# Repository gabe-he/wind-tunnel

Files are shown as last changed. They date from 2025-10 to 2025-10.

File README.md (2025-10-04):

# Wind Tunnel Project

A wind tunnel is a device that produces a controlled stream of air to study how objects interact with airflow, for exploring the principles of aerodynamics.

This project aims to build an accessible, modular educational wind tunnel that can be easily transported and assembled, allowing demonstrations in classrooms, community centers, and public events. By bringing this interactive learning tool to underserved and low-income students, the project seeks to spark curiosity, deepen understanding of science, and inspire the next generation of innovators.

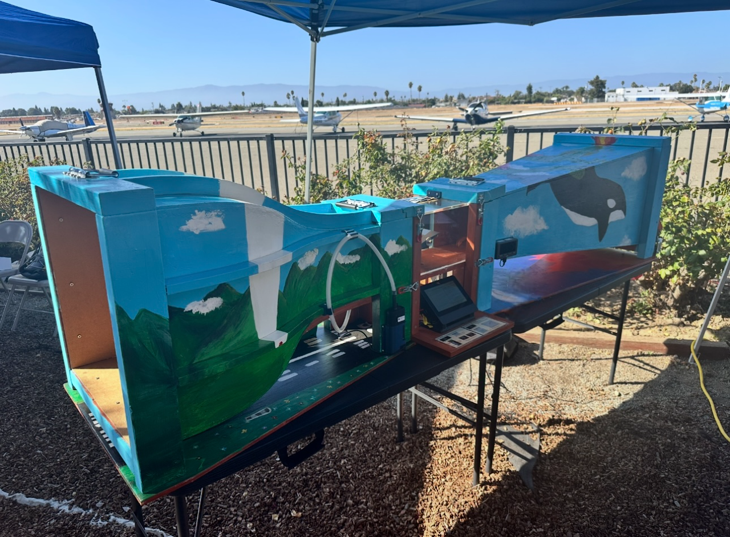
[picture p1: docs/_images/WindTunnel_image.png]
wind tunnel


This repository provides **all resources** related to the wind tunnel project — from planning and design to implementation and analysis. It is intended as a **comprehensive educational package** for anyone interested in building and studying a small-scale aerodynamic experiment. By sharing our design, data, and methods openly, I hope to make hands-on science learning more engaging and approachable for students, educators, and enthusiasts alike.

## Features

* Modular design, can be disassembled for easy transportation
* Adjustable wing angle
* Adjustable airflow speed
* Lift/Drag measurement to measure the lift/drag
* Smoke generator for clear visualization of streamlines
* Demonstrates fundamentals of aerodynamic lift and drag
  * Role of angle of attack in lift generation
  * How flow separation causes stall
  * Visual comparison of laminar vs turbulent flow

## Repository Structure

* [Hardware/](Hardware/) : Hardware design files
* [Software/](Software/) : Software
* [docs/](docs/) : Documentation

### Getting Start

You can start from [docs/](docs/)

### Contributing

Contributions are welcome!

If you have any questions, suggestions, or issues, please don’t hesitate to open an issue.

## Acknowledgements

This project was created by Gabrielle He as the Scout Eagle Project.

⭐️If you like this project, don't forget to give it a ⭐️!

Special thanks to:

* Ms. Catherine Liu @ [cpmentorship](https://www.cpmentorship.org/) – for representing an organization dedicated to mentoring youth and serving the community.
* Mr. Edwin El-Kareh – for his generous assistance and continuous support during the design and build process.
* Mr. Dean McCully @ [EAA62](https://www.eaa62.org/index.php?url=/contact.php) – Young Eagles Coordinator, for helping connect the project to meaningful community service opportunities.
* Mr. David Overhauser – for his expert guidance and instruction throughout the project.
* Mr. Biao – for his hands-on help in constructing the wind tunnel.
* [Troop 688](https://sites.google.com/view/troop688/) – for all the support that made this project possible.

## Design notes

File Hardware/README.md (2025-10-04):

# Hardware

This directory contains the hardware design files for the Wind Tunnel project.

* [windtunnel.FCStd](windtunnel.FCStd) : 3D CAD model of the wind tunnel, created using FreeCAD 1.0.1.
* [BOM.ods](BOM.ods) : Bill of Materials (BOM) of all parts needed to build the wind tunnel. Google sheets exported ods format.
* [BOM_images/](BOM_images/) : Images of parts in the BOM to help identify the parts.
* [Electrical/](Electrical/) : Schematic diagram of the test platform electrical circuit, and some sample images of the circuit.
* [3D_Print/](3D_Print/) : CAD and STL files for 3D printing the custom parts of the wind tunnel.
* [Datasheets/](Datasheets/) : Datasheets of some components used in the wind tunnel.
* [Contraction_Curve_Drawings.pdf](Contraction_Curve_Drawings-desmos.com.pdf) : The Contraction Curve Drawings.

## Build Instructions

User should first read the [Project Plan](../docs/Project_Plan.md) for the detailed design ideas.

Then user can refer to the 3D CAD model file [windtunnel.FCStd](windtunnel.FCStd) to build the wind tunnel hardware. The dimensions in the CAD model are accurate.

If need to know detailed information of each part, check the [BOM](BOM.ods). The part name in the BOM matches the part name in the CAD model.

## Sample Images

overall image of the wind tunnel:

wind tunnel

Sample image for the test platform:

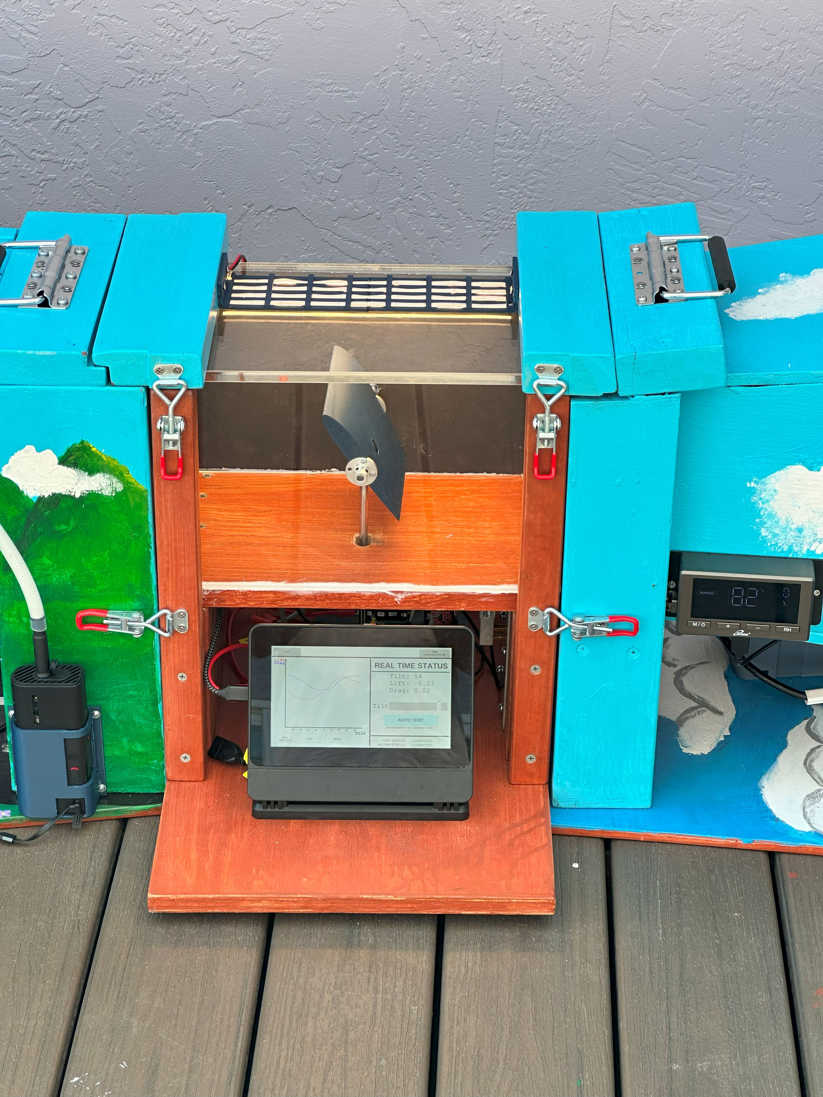
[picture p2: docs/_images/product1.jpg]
test platform


Sample image for the back side of test platform:

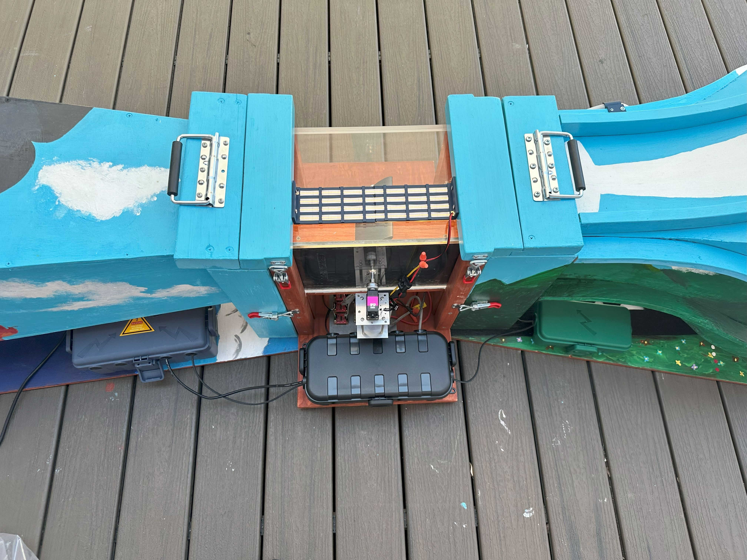
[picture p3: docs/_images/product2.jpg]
test platform back


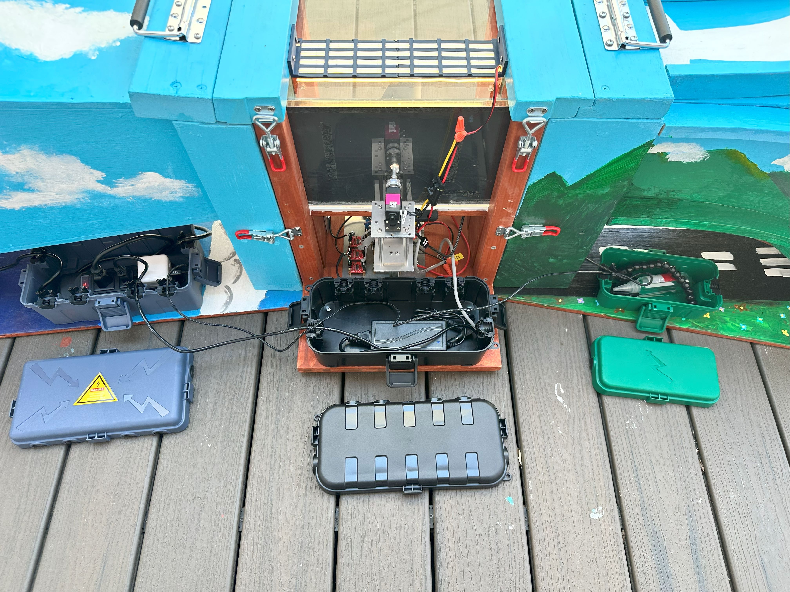
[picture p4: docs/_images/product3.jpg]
test platform back1


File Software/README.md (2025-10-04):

# Software

This is the Software portion of the Wind Tunnel project.

* [RaspberryPi/](RaspberryPi/): The main controller, a Raspberry Pi 4 with touchscreen display.
* [Pico/](Pico/): The microcontroller, a Raspberry Pi Pico, connect to three load cells and output force measurement results to Raspberry Pi 4.

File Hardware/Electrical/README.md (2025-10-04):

# Electrical

This directory contains the Electrical Circuit design files for the Wind Tunnel project.

* [Schematic.pdf](Schematic.pdf): the schematic diagram of the test platform's electrical circuit.
* [Schematic.svg](Schematic.svg): SVG version of same schematic for easy viewing.

The circuit components are mounted on an aluminum plate, using M2/M3/M4 standoffs to separate the components from the surface.

The aluminum plate is then secured to the test platform baseboard using wood screws.

Below is the image of the build::

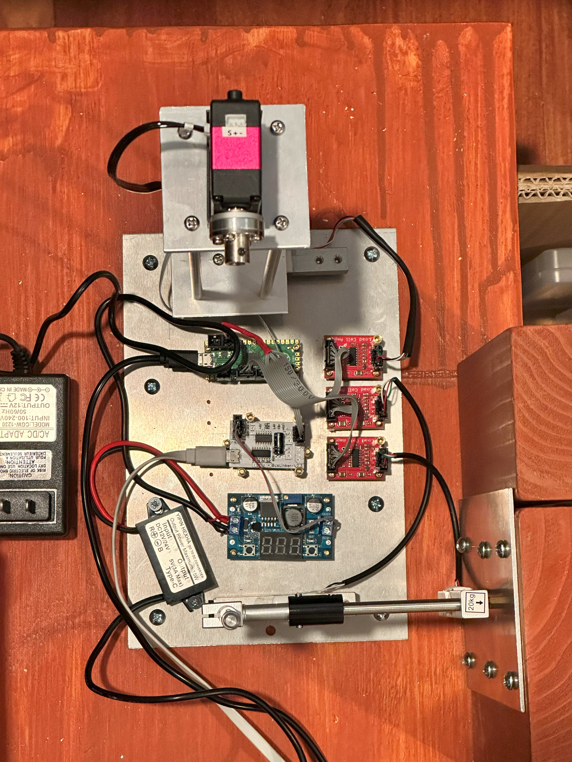
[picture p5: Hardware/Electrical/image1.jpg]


Below is the image before mounting to the baseboard:

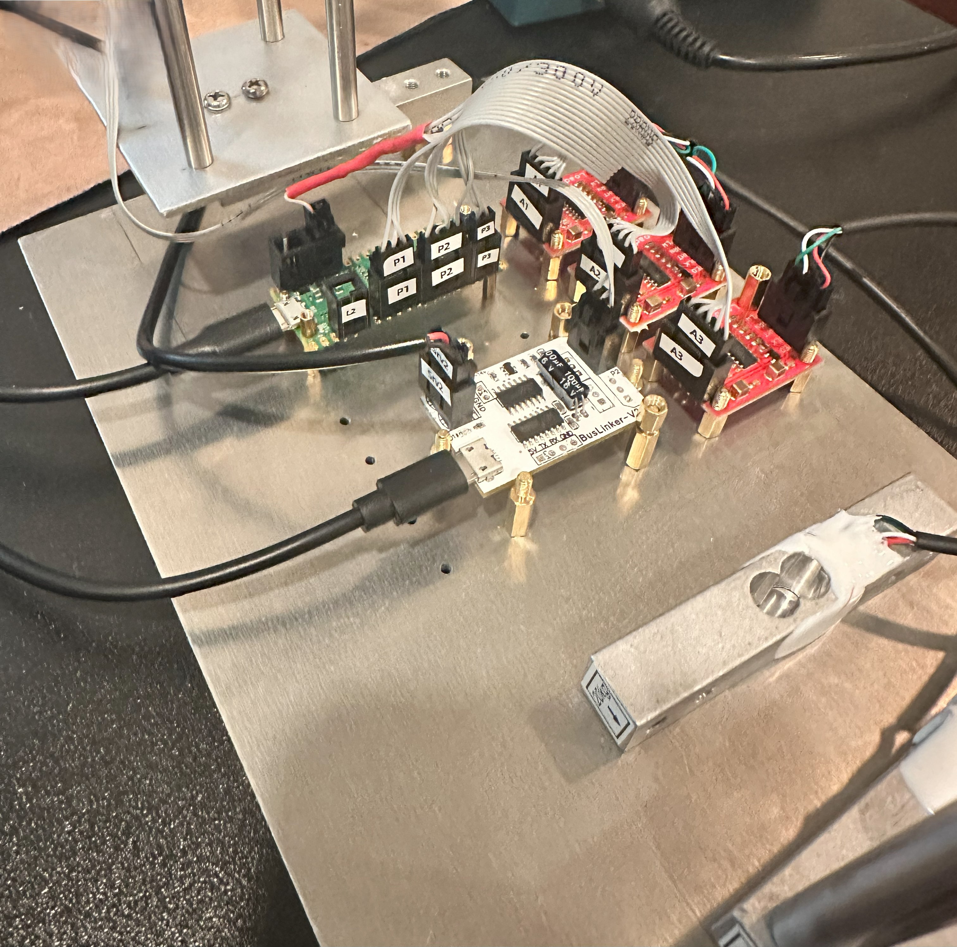
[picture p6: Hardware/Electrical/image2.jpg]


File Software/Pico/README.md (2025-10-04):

# Overview

This is the source code for Raspberry Pi Pico, connect to three load cell and output result to Raspberry Pi 4.

## Hardware

Follow the Schematic to setup the three load cells and HX711 to Raspberry Pi Pico.

## Software

### Install

Follow https://www.raspberrypi.com/documentation/microcontrollers/micropython.html to install the micropython to Raspberry Pi Pico.

use Thonny IDE, copy the four py files to Pico.

### Run

The code will run automatically when Pico is powered on.

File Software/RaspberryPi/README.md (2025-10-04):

# Wind Tunnel Controller

Raspberry Pi is used as the main control interface for the wind tunnel.

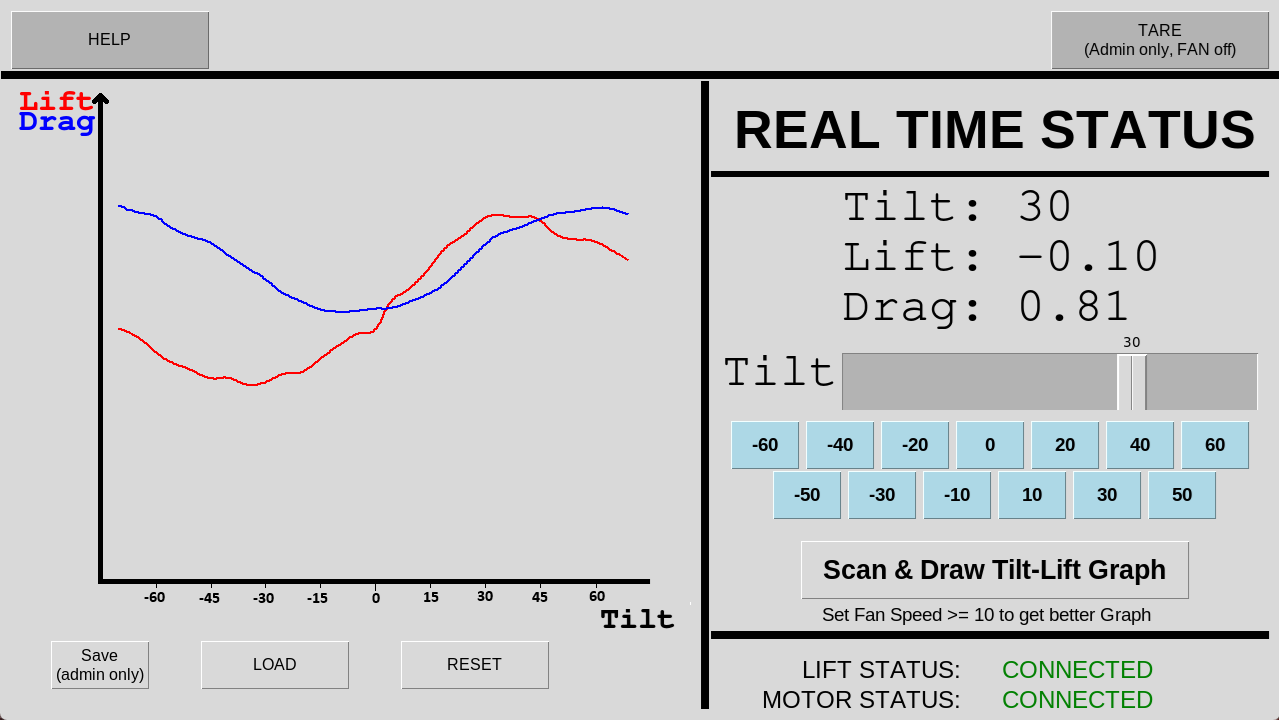
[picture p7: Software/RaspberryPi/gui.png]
wind tunnel controller


## Features

- Touchscreen display
- set Tilt angle
- live update Lift/Drag
- Scan Tilt and draw Tilt vs Lift/Drag graph
- display the Lift/Motor status
- Save/Load graph
- Tare

## Hardware

- Main Controller: 
[Raspberry Pi 4 with 4GB RAM](https://www.raspberrypi.com/products/raspberry-pi-4-model-b/?variant=raspberry-pi-4-model-b-4gb)
- Display: [Official Raspberry Pi Touchscreen Display 2](https://www.raspberrypi.com/products/touch-display-2/)
- Case: [SmartPi Touch Pro 3](https://smarticase.com/collections/smartipi-touch-pro-3/products/smartipi-touch-pro-3)
- 32GB microSD card

### Assemble

Follow the instructions in the official website to install the Raspberry Pi and the display, and assemble the case.

## Software

### Install Raspberry Pi OS

Follow https://www.raspberrypi.com/software/operating-systems/ to install the Raspberry Pi OS for Raspberry Pi 4. I used 64-bit version.

When create user, create username `test` to match the configuration in this repository.

#### Change the display orientation

By default the Touch Display 2 is in portrait orientation. Follow https://www.raspberrypi.com/documentation/accessories/touch-display-2.html to change to landscape:

> If you want to physically rotate the display, or mount it in a specific position, select Screen Configuration from the Preferences menu. Right-click on the touch display rectangle (likely DSI-1) in the layout editor, select Orientation, then pick the best option to fit your needs.

### Install dependencies

1. Install Python: `sudo apt install python3 python3-pip python3-tk`
2. Setup Python environment: `python3 -m pip config set global.break-system-packages true`
3. Install required Python packages: `pip3 install matplotlib pyserial`

### Install Wind Tunnel Controller software

1. Download or clone this repository to **/home/test/wind_tunnel**: `git clone <repository_url> /home/test/wind_tunnel`
2. Copy `WindTunnel.sh` to Desktop for easy access: `cp WindTunnel.sh ~/Desktop/`
3. Copy `99wt.desktop` to autostart so that the software starts automatically when Raspberry Pi boots up:
   `mkdir -p ~/.config/autostart/ && cp 99wt.desktop ~/.config/autostart/`

### Run the software

1. From console: `~/Desktop/WindTunnel.sh`
2. From Desktop: double click `WindTunnel.sh` in the Desktop. Choose "Execute" when prompted.

## FAQ

### Use Raspberry Pi username other than `test`

To use username other than `test`, you need to change the following files:

1. Change the `Exec` in `99wt.desktop` to point to the correct path of `WindTunnel.sh`
2. Change the path in `WindTunnel.sh` to point to the correct path of directory.

### Change the serial port

By default the software uses `/dev/ttyUSB0` as the serial port to connect to the Servo Motor for tilt control. If you want to use a different port, change the `/dev/ttyUSB0` in `WindTunnel.py`.

By default the software uses `/dev/ttyACM0` as the serial port to connect to the Raspberry Pi Pico for force measurement. If you want to use a different port, change the `/dev/ttyACM0` in `WindTunnel.py`.

You can use `dmesg | grep tty` to find out the correct port.

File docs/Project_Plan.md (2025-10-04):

# Wind Tunnel Project Plan

Gabrielle He, 2024 (gabexl.he@gmail.com)

## Table of Contents

* [Project Goal](#project-goal)
* [Project Requirement](#project-requirement)
* [Design Thinking](#design-thinking)
  * [Architecture](#architecture)
  * [Dimensions](#dimensions)
  * [Test platform](#test-platform)
    * [Test room](#test-room)
    * [Test fixture angle adjustment](#test-fixture-angle-adjustment)
    * [Force measurement](#force-measurement)
    * [Controller](#controller)
  * [Contraction](#contraction)
    * [Flow straightener](#flow-straightener)
    * [Smoke generator](#smoke-generator)
    * [Fog fluid](#fog-fluid)
    * [Smoke nozzle](#smoke-nozzle)
    * [Building contraction](#building-contraction)
  * [Diffuser](#diffuser)
    * [Fan](#fan)
    * [Fan safety](#fan-safety)
    * [Building Diffuser](#building-diffuser)
  * [Assemble parts](#assemble-parts)
  * [Electricity](#electricity)
  * [Wood treat](#wood-treat)
    * [Sanding](#sanding)
    * [Filler](#filler)
    * [Paint](#paint)
  * [Seal the gap](#seal-the-gap)
  * [Final product CAD](#final-product-cad)
* [Tools and equipment](#tools-and-equipment)
  * [Powered Tools](#powered-tools)
  * [Hand Tools](#hand-tools)
* [Transportation](#transportation)
* [Safety](#safety)
  * [Tasks for adults only (18+)](#tasks-for-adults-only-\(18+\))
  * [Personal protective equipment](#personal-protective-equipment)
    * [Eye protection](#eye-protection)
    * [Gloves](#gloves)
    * [Masks](#masks)
    * [Closed-toe shoes](#closed-toe-shoes)
    * [Hearing protection](#hearing-protection)
  * [Safety Guidelines](#safety-guidelines)
* [Cost Estimation](#cost-estimation)
* [Citations](#citations)

## Project Goal

The goal of this project is to design and construct a portable wind tunnel that allows for hands-on modeling and exploration of aerodynamics. Compact and easily transportable by car, the wind tunnel is intended to serve a variety of users in different locations. It aims to introduce individuals to the fundamental principles of aerodynamics and the mechanics behind flight. Equipped with an adjustable model plane, the tunnel will enable users to experiment with varying angles and observe their effects, fostering a deeper understanding of how airplanes achieve and sustain flight.

## Project Requirement

1. Features  
   1. Able to demonstrate lift force and drag force of airplane  
   2. Able to change the airplane attack of angle   
   3. Able to adjust the velocity of airflow  
   4. Able to use smoke to visualize the airflow  
   5. Able to use force gauge or load cell to measure the force  
2. Transportation  
   1. Able to transport using normal pickup truck or SUV  
   2. Handles for easy maneuvering the device  
   3. Reasonable strengthening so it can survive a six inch drop.  
3. Safety  
   1. Smoke should be environment friendly. Provide MSDS for the chemical.  
   2. Safety guards for fan blades  
   3. Avoid splinters  
   4. If any glass/mirror is used, consider it’s not easy to break especially during transportation.  
4. Deliverables  
   1. Complete wind tunnel in test and working condition  
   2. Dimensioned drawings and full BOM  
   3. MSDS for all the materials  
   4. Operator’s User Manual  
   5. Manual and warranties of all OEM parts  
   6. All source codes of the software

## Design Thinking

### Architecture

Typical windtunnel will have contraction(where air comes in), test platform and diffuser(where air be pulled out).

This is a reference commercial wind tunnel:

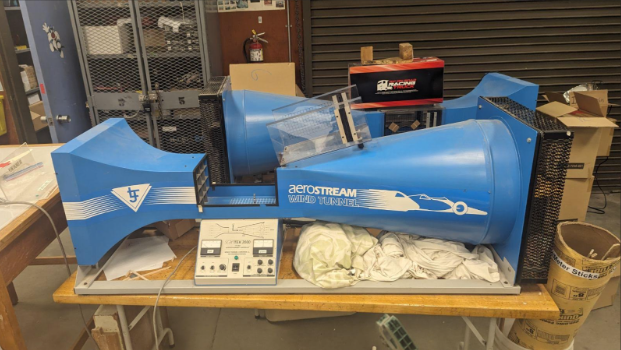
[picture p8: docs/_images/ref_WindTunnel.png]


### Dimensions

The reference product in the image above has overall dimensions 1730mm(L) \* 550mm(H) \* 550mm(W), test platform dimensions 300mm(L) \* 200mm(H) \* 200mm(W).

This project will have similar dimensions, overall 2500mm(L) \* 620mm(H) \* 550mm(W), test platform dimensions 300mm(L) \* 200mm(H) \* 200mm(W).

Considering the easy transportation of the wind tunnel, this project will make separate contraction, test platform and diffuser, and make sure they’re easy to install in the field. The sealing between the three parts will be discussed later.

The dimension of the three parts is:

1. Contraction: 1060mm(L) \* 550mm(H) \* 580mm(W)  
2. Test platform: 440mm(L) \* 500mm(H) \* 550mm(W)
3. Diffuser: 1450mm(L) \* 550mm(H) \* 550mm(W)

The contraction and diffuser have different widths in two ends. For contraction, the opening end is 550mm and the test platform end is 300mm. For Diffuser, the opening end is 550mm and the test platform end is 300mm.

Top view of the parts:

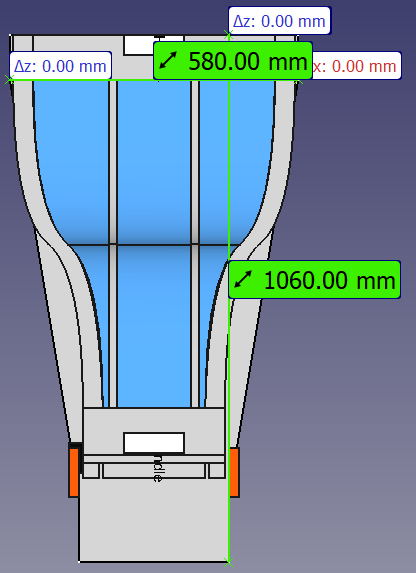
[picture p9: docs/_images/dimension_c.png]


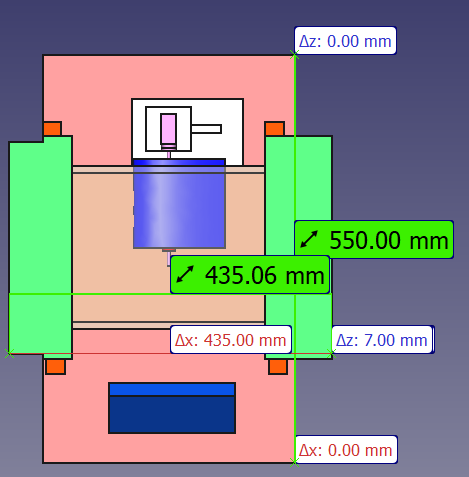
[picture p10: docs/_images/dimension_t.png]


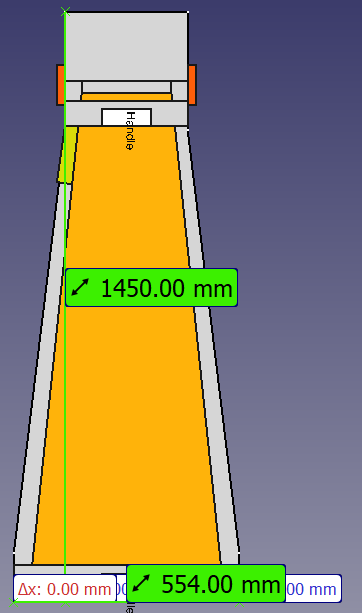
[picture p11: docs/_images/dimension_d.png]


For how to transport the wind tunnel, please see [Transportation](#transportation) chapter later.

### Test platform

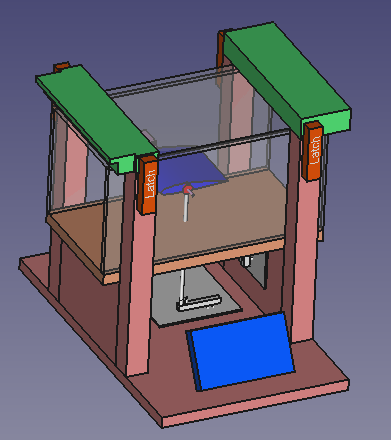
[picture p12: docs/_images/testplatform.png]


Test platform is where the test device gets wind, and then the user measures the forces.

#### Test room

The test room is 400mm(L) \* 200mm(W) \* 200mm(H), the visible are is 300mm(L) \* 200mm(W) \* 200mm(H), because it needs some space at the two ends to connect to the contraction and diffuser.

The test room bottom is made of wood. The front/back/top sides are made with acrylic. **10mm** thick acrylic boards are used, to have enough strength. I thought about having a mirror at the rear side of the test room, but then I realized the mirror is easy to break, and just having acrylic to allow the other user to see the test device from the other side of the wind tunnel is also sufficient.

The top acrylic board can be opened, so the end user can reach the objects on the test fixture.

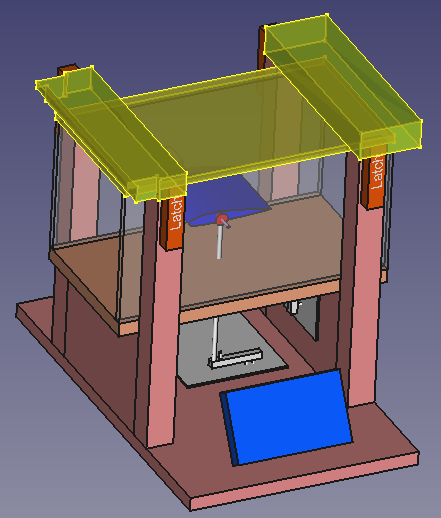
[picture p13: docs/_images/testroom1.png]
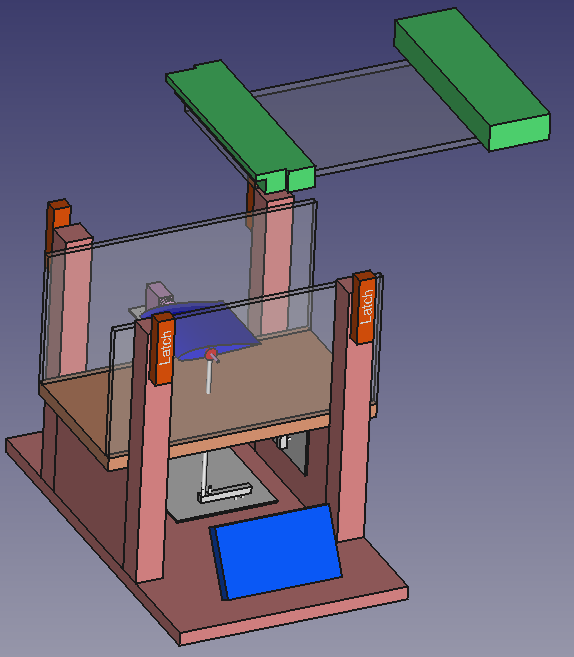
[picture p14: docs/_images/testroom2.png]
 

Toggle latch will be used to fix the top cover to the test room after it’s closed.

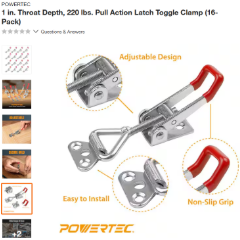
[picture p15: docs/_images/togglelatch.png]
 [POWERTEC 220 lbs. Pull Action Latch Toggle Clamp](https://www.homedepot.com/p/POWERTEC-220-lbs-Holding-Capacity-Pull-Action-Latch-Toggle-Clamp-4001-with-Red-Vinyl-Handle-Grip-32-Pack-20332-P4/321600330#overlay)

Below image shows the top locked during the test. RED rectangles are for toggle clamps.

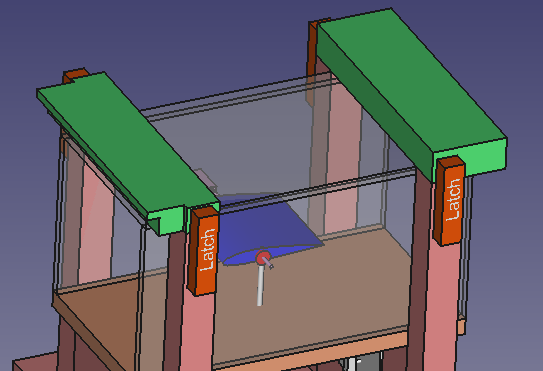
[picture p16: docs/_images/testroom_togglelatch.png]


#### Test fixture angle adjustment

Adjusting the device angle of attack is a very important feature this project will support.

A servo motor is used to adjust the angle.

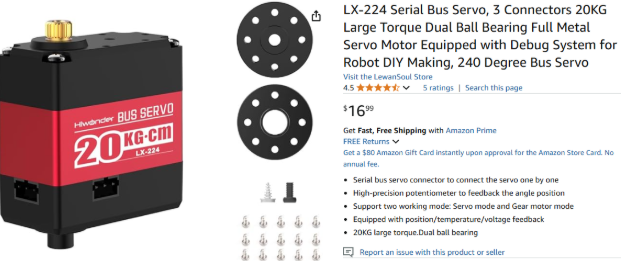
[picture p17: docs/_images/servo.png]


This motor supports 240 degree angle change and position feedback.

The motion will connect to a rod, in the other end of the rotation rod, a Rod End Bearing is used.

To prevent the large drag caused by the motor, I put the motor out of the test room, only the test fixture is inside the test room. This can significantly reduce the drag caused by items other than test devices.

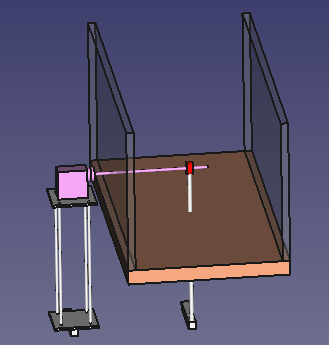
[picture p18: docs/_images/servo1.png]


#### Force measurement

Strain gauge load cell is used to measure the force(both lift force and drag force).

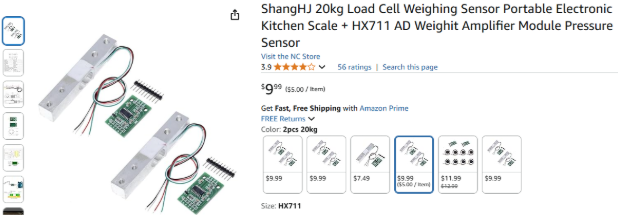
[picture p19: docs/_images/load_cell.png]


A typical load cell setup is like below, it can measure the force on the top plate(both push and pull). Ref: [Load Cell Guide \- Phidgets Support](https://www.phidgets.com/docs/Load_Cell_Guide)

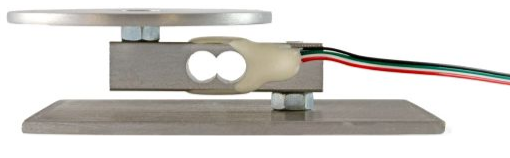
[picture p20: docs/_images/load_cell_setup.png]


For the lift force, it may distribute to both the servo motor and the main VRod(vertical Rod). So we add load cells to both the servo motor and VRod, and add them together. This will be more accurate to measure the lift. See “Lift Cell1” and “Lift Cell2” below. Update: only "Lift Cell2" is used now.

For the drag force, one load cell is used, see “Drag cell” below.

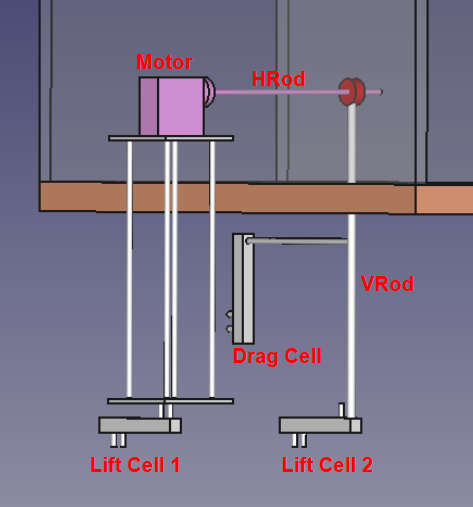
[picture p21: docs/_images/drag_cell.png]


The load cell output will be connected to the load cell amplifier (HX711) and then connect to the Raspberry Pi.

#### Controller

Raspberry Pi is used as the main controller for the wind tunnel.

HW: Raspberry Pi 4 with 7” display.

The Raspberry Pi HW will connect to three load cells and one Servo Motor.

The SW on Raspberry Pi GUI will allow user to:

1. Control Servo Motor to set the angle of attack  
2. Read three load cells and display the lift force and drag force  
   1. Need a reset button after install the test device to reset the force to 0

For the detailed HW circuit and SW design guide, will update later.

To secure the controller on the base board, I will consider it later. This should not be a big problem.

### Contraction

Contraction: incline of 14 degrees 

- Entrance dimensions: width 500mm \* height 500mm  
- Exit dimensions: width 200mm \* height 200mm  
- Total length: 600mm

The incline rates are similar to suggestions in the research below. Though the rates are not exactly the same as the resource, the resource states the 12 degrees as having “reasonable length and good fluid dynamics”.  
[Resource](https://www.intechopen.com/chapters/43210)

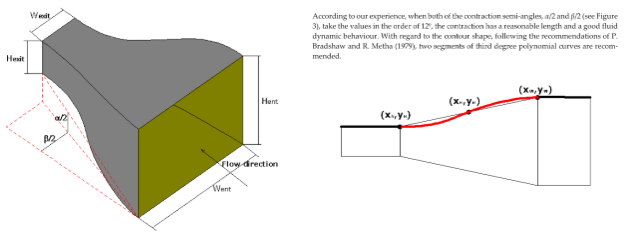
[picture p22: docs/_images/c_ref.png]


The Contraction CAD view:

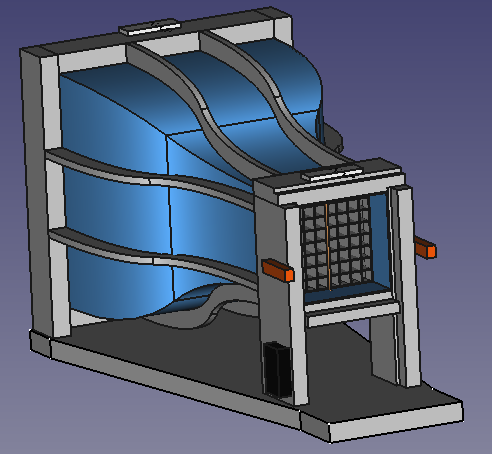
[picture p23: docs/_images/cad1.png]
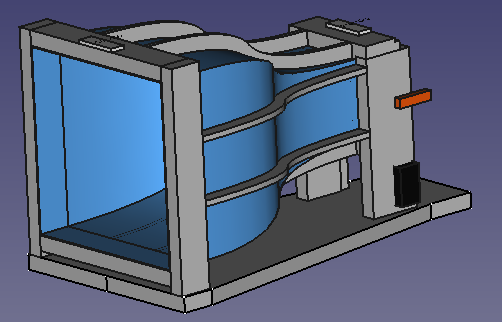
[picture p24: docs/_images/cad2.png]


#### Flow straightener

In the contraction to test platform there’s an air flow straightener to control the airflow, avoid turbulence.

I'll use 3D printer to print the flow straightener.

#### Smoke generator

After the rear flow straightener, there's a smoke machine to generate smoke for airflow visualization.

The smoke generator below will be used.

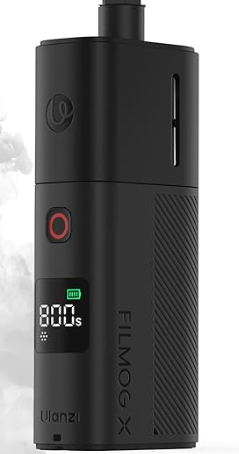
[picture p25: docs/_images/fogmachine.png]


This smoke generator has a start button.

#### Fog fluid

The smoke generator needs fog fluid to generate the smoke.

[SDS](https://www.froggysfog.com/media/files/sds/bog-fog-extreme-density-fog-fluid-sds-us-102014-final.pdf)

It's non-toxic, water based, and environmentally friendly.

#### Smoke nozzle

Smoke nozzle is where the smoke gets out. It’ll be installed just after the rear air straightener.

The nozzle will installed like this:



There will be small holes on the nozzle, so the smoke can come out evenly.

#### Light Strip

For easy visualization of the smoke, a light strip will be installed on top of the test platform cover. And the test platform backside will be covered by black paper.

The light strip will be hot, so will not fully cover the light strip.

#### Building contraction

To have better airflow, the contraction is in curve shape, not trapezoid. This causes it’s not easy to build. This chapter records my idea on how to build the contraction.

1. Build the connections to the test platform. Make sure the size matches the test platform entrance size.



2. Build the 8 contraction support.



3. Install the side wall of contraction



4. Temporary fix the opening, and cut the side wall



5. Remove the side wall, and do the same for the top/down wall



6. Remove temporary opening fix, and install all the four walls



7. Fix the opening



8. Install the base



### Diffuser

Diffuser: incline of 4.7 degrees

- Entrance dimensions: width 200mm \* height 200mm  
- Exit dimensions: width 400mm \* height 400mm  
  - Fit for 16in fan dimensions (see link)  
  - [Fan](https://www.homedepot.com/p/iLIVING-1736-CFM-DC-Motor-Gray-16-in-Wall-Mounted-Shutter-Exhaust-Fan-with-Temperature-and-Humidity-Controls-Variable-Speed-ILG8SF16V-DC/329655167)  
- Total length: 1300mm

Corresponding with images of other wind tunnels (ie. see image above), most modern wind tunnels have a contraction and differ angles slightly larger than the resource recommendation.

#### Fan

This fan is used for diffuser:



The fan is 1200 CFM(cubic feet/minute), our test platform is 200mm(W) \* 200mm(H), it means the air speed in the test platform is 1200 \* 300mm \* 300mm \* 300mm / 200mm / 200mm / 60s \= 13500 mm/s \= 13.5m/s. According to [Beaufont scale chart](https://en.wikipedia.org/wiki/Beaufort_scale), it’s wind force 6, strong breeze. It’s quite good for this project.  


And this Fan supports variable speed control, we can also test different drag/lift force under different air speed.

#### Fan safety

When the fan is running, the blade is dangerous. To avoid kits touching the blade causing any injury, I plan to install a mesh after the fan. The opening of the mesh should \<= ¼” to avoid fingers getting in.



And I’ll try to leave some space between Fan and mesh, like 50mm. It’s not shown in current CAD design, but the fan blade safety will be seriously considered.

#### Building Diffuser

Build diffuser is easier than build contraction, because it’s straight, no curve.

### Assemble parts

The final wind tunnel after assemble is as below:



The same toggle latches used in the test room top cover will be used for the parts connections:



### Electricity

All of the three parts need electrical:

1. Diffuser: Exhaust Fan, 110V 1A.
2. Contraction: Smoke Generator, 5V 2A
3. Test platform: Most likely 12V 2A

This cord will be used to bring external power to the wind tunnel.



It’s rated 15 Amps, good enough.

The overall power system design as below:



1. Power cord to two outlet boxes
   1. The power cord can be stored under Diffuser when not used.
2. Smoke generator power cord connect to outlet when in use
   1. There’s cable management clips on back of test platform to hold the smoke generator power cord
   2. When smoke generator not in use, the power cord can be stored under Contraction
3. Test platform power cable is short.
   1. When not in use, the power cable should also be stored well. Will come out with a solution later.

### Wood treat

My original idea is to use the most cost efficient 2x4 construction lumber for most of the materials. This lumber is less than $4 for 2x4 8ft. But after checking these lumbers, I found these lumbers are too rough and splintery.

2x4 lumber:



The new idea is to use redwood, which has much less splinters and a smoother surface.

2x4 redwood lumber:



And to cut the wood as less as possible, I’ll use wood original width and thickness so I only need to cut length. The standard wood size is in the table below.

| Nominal Size (Inches) | Actual Size (Inches) | Actual Size (mm) | Quantity (ft) |
| :---- | :---- | :---- | :---- |
| 1 x 2 | 3/4 x 1 1/2 | 19 x 38 | 6 |
| 1 x 3 | 3/4 x 2 1/2 | 19 x 64 |  |
| 1 x 4 | 3/4 x 3 1/2 | 19 x 89 | 2 |
| 1 x 6 | 3/4 x 5 1/2 | 19 x 140 |  |
| 2 x 2 | 1 1/2 x 1 1/2 | 38 x 38 | 9 |
| 2 x 3 | 1 1/2 x 2 1/2 | 38 x 64 | 4 |
| 2 x 4 | 1 1/2 x 3 1/2 | 38 x 89 | 28 |
| 2 x 6 | 1 1/2 x 5 1/2 | 38 x 140 | 1 |

This redwood lumber is $15 for 2x4 8ft. Using redwood will increase the wood material cost from original estimation $32 to \~$100. But I think this is worth doing. It can save me much time to smooth the surface, and the final product will be very beautiful.

With this redwood lumber, we still need a process to make it smooth and splinter free. These steps are needed:

1. Sanding  
2. Filler  
3. Paint  
   1. Finish the surface with a non-toxic paint.

#### Sanding

Sander machine will be used first, to make the surface smooth.



Sandpaper has different grits for different purposes.



For this project, 80 grit will be used first to rough treat the wood, and then 220 grit to fine finish.

#### Filler

If there’s any cracks or knots in the wood, fill with wood filler and then smooth it again.



#### Paint

Paint happens after the assembly is done.

There are many types of paint available. To be health and environment friendly, we’ll use non-toxic water-based coatings. I’d like to keep the original wood color, so I plan to use a redwood color semi-transparent waterproof exterior wood stain and sealer.



[SDS](https://images.thdstatic.com/catalog/pdfImages/27/27f3fb64-bb87-412c-aa3a-92196bf9af9d.pdf)

### Seal the gap

There would be a gap between the board connections, especially between the Contract and Diffuser front/rear/top/bottom boards. We want to seal the gap to avoid air leakage.

For small gaps \<= 5mm, wood filler used in the previous chapter can be used to fix the gap as well.

Sealant/Caulk is also possible but it’s different to sand and paint.

If the gap is really big, we should consider fixing this by the board itself, maybe discard the broken board and make a new one.

### Final product CAD

Front view:



Top view:


Bottom view:


Rear view:



Left view:



Right view:



Top-Front-Right view:



Top-Rear-Left view:



## Tools and equipment

### Powered Tools

| Name | Purpose | Comment |
| ---- | ----    | ---- |
| Table Saw | Cutting wood | Used by adult only |
| Circular Saw | Cutting wood | Used by adult only |
| Jigsaw | Fine cutting wood | Used by adult only |
| Sander | Smooth wood |  |
| Cordless Screwdriver | Fasten screw |  |
| Cordless Drill | Making holes |  |

### Hand Tools

| Name | Purpose | Comment |
| ---- | ---- | ---- |
| Wrench | Fasten |  |
| Tape measure | Measurement |  |
| Pencil | Mark the position on wood |  |
| Welding toolkit | For copper tube |  |
| Paint brush | Painting |  |

Personal safety tools will be mentioned in the safety chapter later.

## Transportation

This page list the popular SUV cargo space: [https://www.mcgrathauto.com/suv-cargo-space.htm](https://www.mcgrathauto.com/suv-cargo-space.htm)

This table is in inches (mm):

|  | Ford Escape | Ford Edge | Subaru Outback | Toyota Highlander | Toyota Sienna |  |
| :---- | :---- | :---- | :---- | :---- | :---- | :---- |
| Door width | 43 in (1092 mm) | 47 in (1193 mm) | 44 in (1117 mm) | 45.5 in (1155 mm) | 50 in (1270 mm) |  |
| wheel-to-wheel width | 41.5 in (1054 mm) | 45 in (1143 mm) | 42 in (1066 mm) | 45.5 in (1155 mm) | 49 in (1244 mm) |  |
| height | 35 in (889 mm) | 32 in (812 mm) | 29.5 in (750 mm) | 29.5 in (750 mm) | 38.5 in (977 mm) |  |
| Length (2nd row fold down) | 67 in (1700 mm) | 72.5 in (1841 mm) | 61 in (1549 mm) | 83.5 in (2120 mm) | 94 in (2387 mm) |  |

All these models have enough height for the 650mm height wind tunnel.

With a reasonable gap between parts, the setup can be arranged like below(top view). The three parts need 1122mm(W) \* 1480mm(L) space, it’s good enough for all the SUVs listed above.



To make maneuvering the device easier, I added some handles in Contraction and Diffuser.

I plan to use this handle below:  


NOTE: Not recommended to move the whole wind tunnel together. Always disassemble into three parts(Contraction, Test Platform, Diffuser) and move separatedly.

## Safety

Safety is the most important thing during construction.

### Tasks for adults only (18+)

1. Power cutting tools
   1. Table saw
   2. Circular saw
   3. Jigsaw
2. Electrical work
   1. Connecting 110V AC power circuits
   2. Soldering high voltage connectors
   3. Final connection to wall power

### Personal protective equipment

#### Eye protection

Safety glasses must be worn at all times near power tools.

#### Gloves

Gloves should be worn when handling wood and paint. However, gloves should be avoided when using power tools with spinning blades or bits, as they can get caught and cause injury.

#### Masks

Use dust masks when cutting wood, sanding, and applying paint.

#### Closed-toe shoes

Closed toe shoes are required all the time.

#### Hearing protection

Optional when power saw is in operation.

### Safety Guidelines

1. Scouts should not operate a tool without adult permission and supervision
2. Only one person operates a power tool at a time \- no distractions allowed.
3. All tools must be unplugged when changing bits, blades, or making adjustments.
4. Extension cords must be secured to avoid tripping hazards.
5. Do not run or play in working area
6. All 110V connections must be done by adults
7. Never put water or drinks close to any electrical

## Cost Estimation

See BOM file.

## Citations

- Wittwer, Adrián Roberto, et al. “Statistical Analysis of Wind Tunnel and Atmospheric Boundary Layer Turbulent Flows.” IntechOpen, 6 Mar. 2013, www.intechopen.com/chapters/43210. Accessed 25 Dec. 2024\.

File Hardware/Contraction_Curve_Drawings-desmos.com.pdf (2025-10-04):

## How to Use

Print each page at letter size, without scale.

Then put three pages together on the board, the curve is for Contraction side support curve.





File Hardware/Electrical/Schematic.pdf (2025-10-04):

## PWR

A1


Connector | Type
C1, C2, C3 | 4 pin connector
A1, A2, A3 | 5 pin connector
P1 | 3 pin connector
P2 | 4 pin connector
P3 | 2 pin connector
PWR | 4 pin connector
Cell Pin | RPi Pico Pin
Cell A1 DAT | GP6
Cell A1 CLK | GP7
Cell A2 DAT | GP9
Cell A2 CLK | GP10
Cell A3 DAT | GP11
Cell A3 CLK | GP13
P1 | P2 | P3

A2

A3

C1

## TPLoadCell0

TPLoadCell1 | TPLoadCell2

C2

C3

## TPServo

## TPServoDB

## TPDC7V5

## TPDC5V

## Touch Display

## Raspberry Pi 4

## TPDC12V

## 110V AC POWER Input

12V

7.5V

5V

# USB

# USB

## LoadCellAmp

## Raspberry Pi Pico

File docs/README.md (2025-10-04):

# Documents

This directory contains the documentation for the Wind Tunnel project.

* [Project Plan](docs/Project_Plan.md) : Detailed project plan, design considerations, build instructions, and safety guidelines.
* [User Guide](docs/User_Guide.png) : Instructions for end user to use the wind tunnel.
* [Installation Guide](docs/Installation_Guide.png) : Instructions for product owner to assemble and install the wind tunnel.

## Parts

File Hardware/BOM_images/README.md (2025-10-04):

# BOM Images

This directory contains images for the BOM components.

| BOM/CAD Name | Preview | Filename | Comment |
|------|---------|----------|---------|
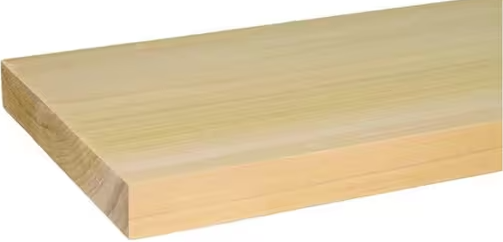
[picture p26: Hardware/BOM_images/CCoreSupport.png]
CCoreSupport
| CCoreSupport |  | [CCoreSupport.png](CCoreSupport.png) | |
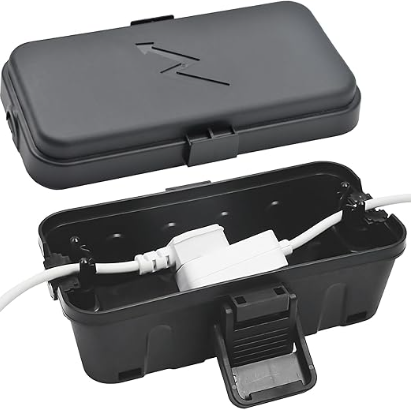
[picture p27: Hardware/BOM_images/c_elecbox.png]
c_elecbox
| CElecBox |  | [c_elecbox.png](c_elecbox.png) | |
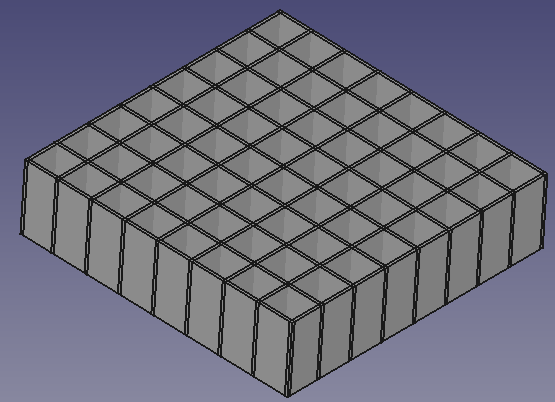
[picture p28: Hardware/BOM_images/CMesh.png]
CMesh
| CMesh |  | [CMesh.png](CMesh.png) | |
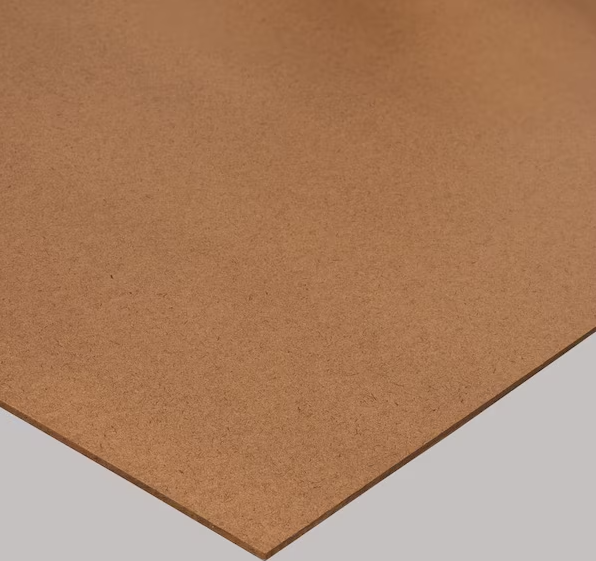
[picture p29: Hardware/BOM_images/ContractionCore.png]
ContractionCore
| ContractionCore |  | [ContractionCore.png](ContractionCore.png) | |
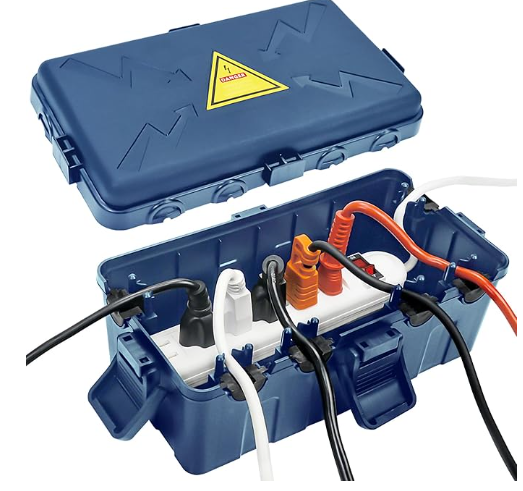
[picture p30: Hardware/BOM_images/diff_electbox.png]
diff_electbox
| DElecBox |  | [diff_electbox.png](diff_electbox.png) | |
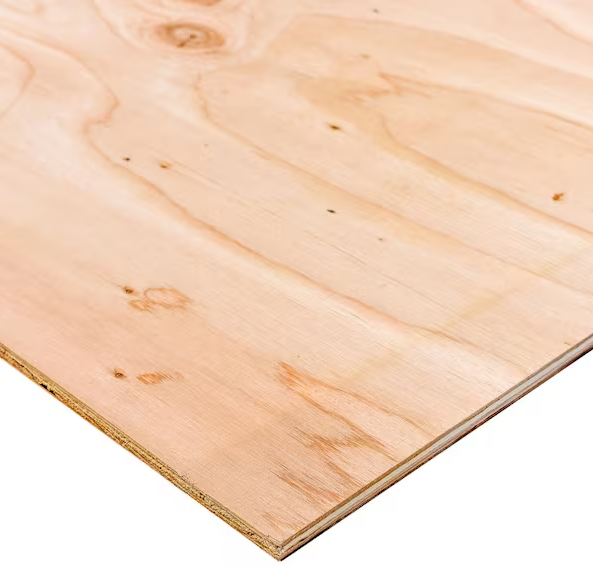
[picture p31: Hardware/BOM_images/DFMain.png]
DFMain
| DFMain |  | [DFMain.png](DFMain.png) | |
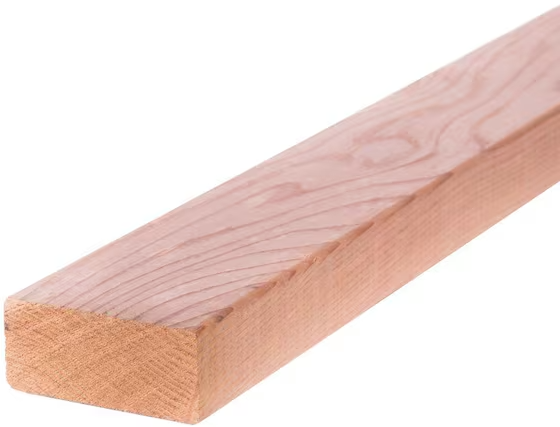
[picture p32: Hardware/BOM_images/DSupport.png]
DSupport
| DS001 |  | [DSupport.png](DSupport.png) | |
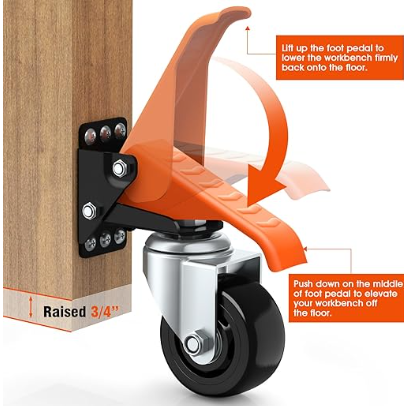
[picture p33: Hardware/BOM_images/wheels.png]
wheels
| DWheel |  | [wheels.png](wheels.png) | |
| Fan | Fan | [Fan.png](Fan.png) | |
| FanConnector | FanConnector | [FanConnector.png](FanConnector.png) | |
| FanMesh0 | FanMesh0 | [FanMesh0.png](FanMesh0.png) | |
| FanMesh1 | FanMesh1 | [FanMesh1.png](FanMesh1.png) | |
| Handle | Handle | [Handle.png](Handle.png) | |
| Latch | Latch | [Latch.png](Latch.png) | |
| LoadCellAmp | LoadCellAmpImage | [LoadCellAmpImage.png](LoadCellAmpImage.png) | |
| Paint | AcrylicPaint | [AcrylicPaint.png](AcrylicPaint.png) | |
| RaspberryPi4 | RaspberryPi4 | [RaspberryPi4.png](RaspberryPi4.png) | |
| RaspberryPiPico | RaspberryPiPicoImage | [RaspberryPiPicoImage.png](RaspberryPiPicoImage.png) | |
| Screws | screws | [screws.png](screws.png) | |
| Sealant | Sealant | [Sealant.png](Sealant.png) | |
| Sealer | Sealer | [Sealer.png](Sealer.png) | |
| SmartPiTouchPro3 | SmartPiTouchPro3 | [SmartPiTouchPro3.png](SmartPiTouchPro3.png) | |
| SmokeCharger | usbc | [usbc.png](usbc.png) | |
| SmokeCopper | smokecopper | [smokecopper.png](smokecopper.png) | |
| SmokeGenerator | fogmachine | [fogmachine.png](fogmachine.png) | |
| SmokeTube | smoketube | [smoketube.png](smoketube.png) | |
| Spacers | Spacers | [Spacers.png](Spacers.png) | |
| TElecBox | test_elecbox | [test_elecbox.png](test_elecbox.png) | |
| TouchDisplay2 | TouchDisplay2 | [TouchDisplay2.png](TouchDisplay2.png) | |
| TPAluBottom | TPAluBottom_Image | [TPAluBottom_Image.png](TPAluBottom_Image.png) | |
| TPBottom | TPBottom1x12 | [TPBottom1x12.png](TPBottom1x12.png) | |
| TPBottomSupport | TPBottomSupport | [TPBottomSupport.png](TPBottomSupport.png) | |
| TPDC12V | dc12v | [dc12v.png](dc12v.png) | |
| TPDC5V | TPDC5V | [TPDC5V.png](TPDC5V.png) | |
| TPDC7V5 | TPDC7V5 | [TPDC7V5.png](TPDC7V5.png) | |
| TPDrag0 | TPDrag0 | [TPDrag0.png](TPDrag0.png) | |
| TPDrag1 | TPDrag1 | [TPDrag1.png](TPDrag1.png) | |
| TPDrag2 | TPDrag2 | [TPDrag2.png](TPDrag2.png) | |
| TPHRod | TPHRodImage | [TPHRodImage.png](TPHRodImage.png) | |
| TPHVBearing | TPHVBearingImage | [TPHVBearingImage.png](TPHVBearingImage.png) | |
| TPLoadCell | TPLoadCellImage | [TPLoadCellImage.png](TPLoadCellImage.png) | |
| TPLoadCellSpec1 | TPLoadCellSpec1 | [TPLoadCellSpec1.jpg](TPLoadCellSpec1.jpg) | |
| TPLoadCellSpec2 | TPLoadCellSpec2 | [TPLoadCellSpec2.jpg](TPLoadCellSpec2.jpg) | |
| TPServo | TPServo_Image | [TPServo_Image.png](TPServo_Image.png) | |
| TPServoAluBase | TPServoAluBase_Image | [TPServoAluBase_Image.png](TPServoAluBase_Image.png) | |
| TPServoDB | TPServoDB_Image | [TPServoDB_Image.png](TPServoDB_Image.png) | |
| TPServoDisc | TPServoDisc | [TPServoDiscImage.png](TPServoDiscImage.png) | |
| TPServoFlange | TPServoFlangeImage | [TPServoFlangeImage.png](TPServoFlangeImage.png) | |
| TPServoSupport | TPServoSupport | [TPServoSupport.png](TPServoSupport.png) | |
| TPSupport | TPSupport2x2 | [TPSupport2x2.png](TPSupport2x2.png) | |
| TPVRod | TPVRodImage | [TPVRodImage.png](TPVRodImage.png) | |
| TSecBase | TSecBase | [TSecBase.png](TSecBase.png) | |
| Wing | wing | [wing.png](wing.png) | |

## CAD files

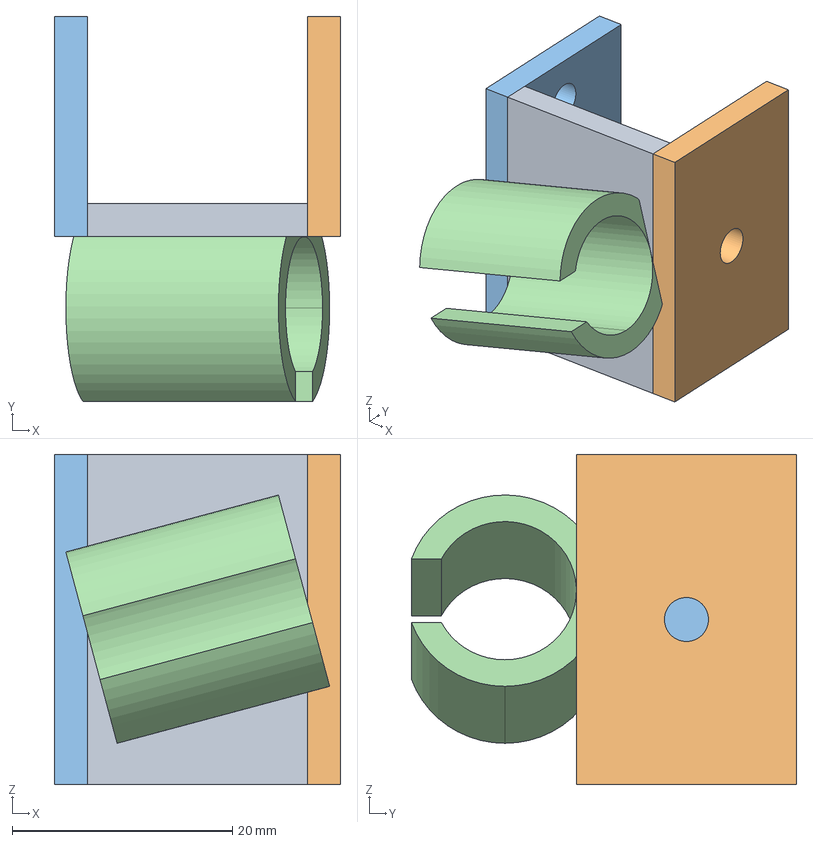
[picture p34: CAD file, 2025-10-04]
Hardware/3D_Print/smokePipeClamp2.FCStd
26.0 x 35.0 x 30.0 mm

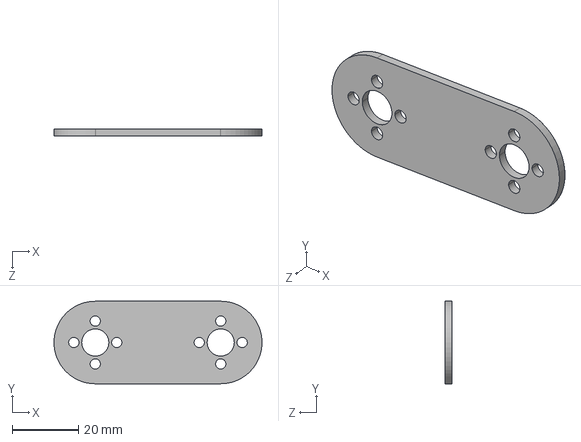
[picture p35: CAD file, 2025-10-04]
Hardware/Datasheets/Servo/TPServo_LX224/3. Servo Manual & Diagram/3. Drawings/Bracket/IGS/One-frame bracket.IGS
63.0 x 25.0 x 2.00 mm

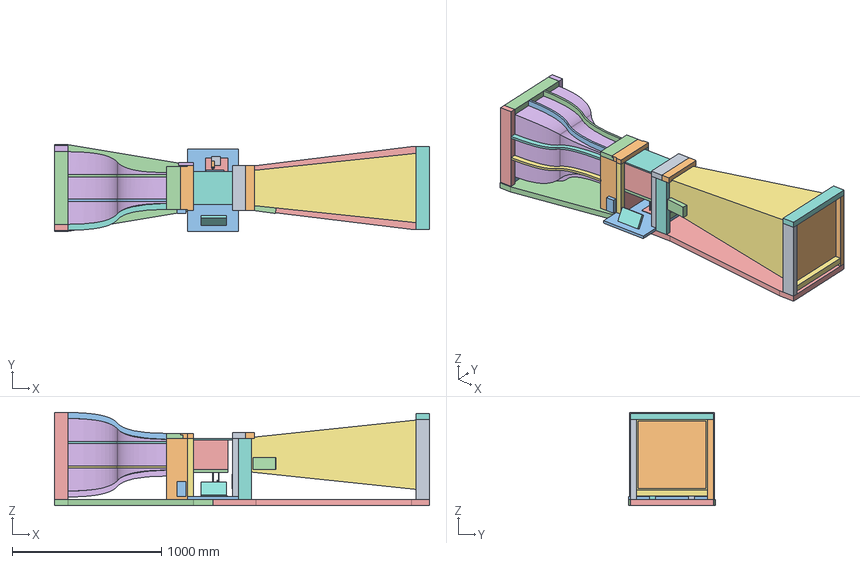
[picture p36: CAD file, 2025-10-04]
Hardware/windtunnel.FCStd
2510.0 x 580.0 x 623.0 mm
wing
TPBottom
TPGlass_Front
TPGlass_Back
DTS003
DTS001
DTS002
DTS004
CS001
CS002
CS003
CS004
DS001
DS002
DS003
DS004
TestElec
TPBottomSupport1
TPBottomSupport2
TPLoadCell0
TPLoadCell2
Display
TPServoAluBase
TPServo
TPLoadCell1
TPLoadCell1Top
TPAluBottom
Alu_Bottom001
TPSupport1
TPSupport2
TPSupport3
TPSupport4
SmokeGenerator
FanButton
Latch002
Latch004
Latch007
Latch010
Latch013
Latch015
Latch020
Latch021
Handle
Handle002
Handle004
Handle006
CTS001
CTS002
CTS003
CTS000
TPVRod
TPHRod
TPHVBearing
TPServoSupport4
TPServoSupport3
TPServoSupport1
TPServoSupport2
SmokeBottom
TPServoDisc
TPServoFlange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

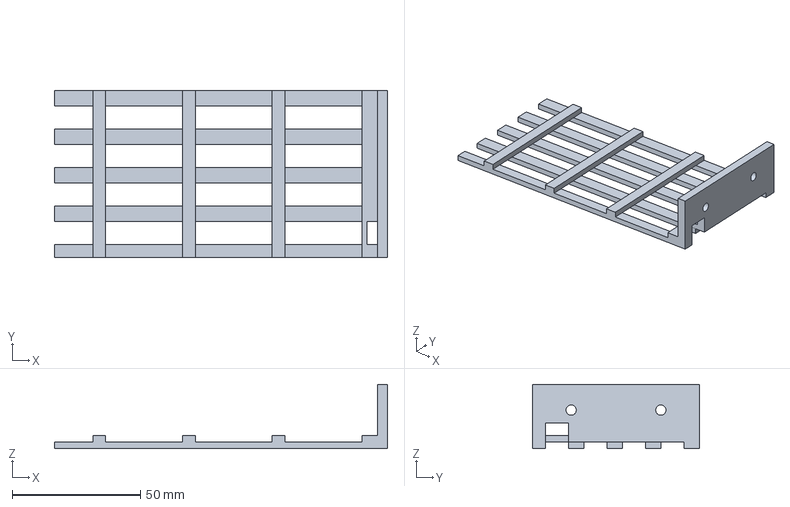
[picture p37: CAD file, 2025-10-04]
Hardware/3D_Print/light_strip.FCStd
130.0 x 65.0 x 25.0 mm

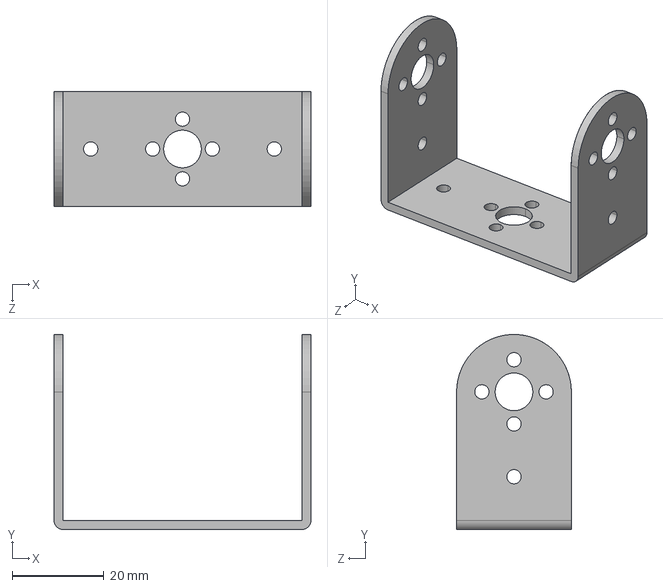
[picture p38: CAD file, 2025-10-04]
Hardware/Datasheets/Servo/TPServo_LX224/3. Servo Manual & Diagram/3. Drawings/Bracket/IGS/U backet-short.IGS
56.0 x 42.5 x 25.0 mm

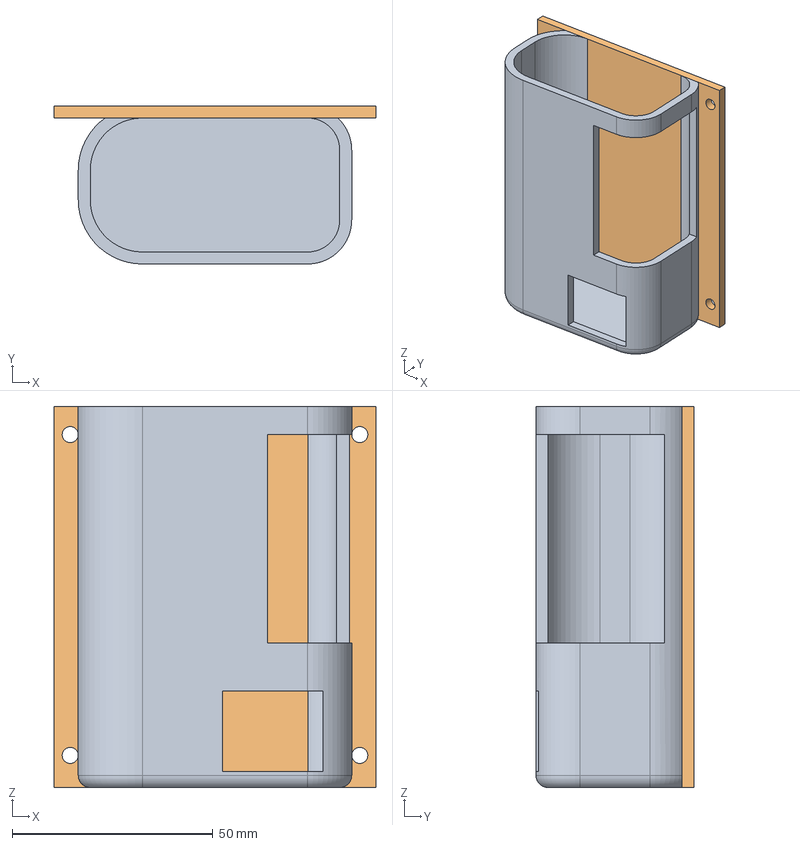
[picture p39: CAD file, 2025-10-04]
Hardware/3D_Print/smoker.FCStd
80.2 x 39.4 x 95.0 mm

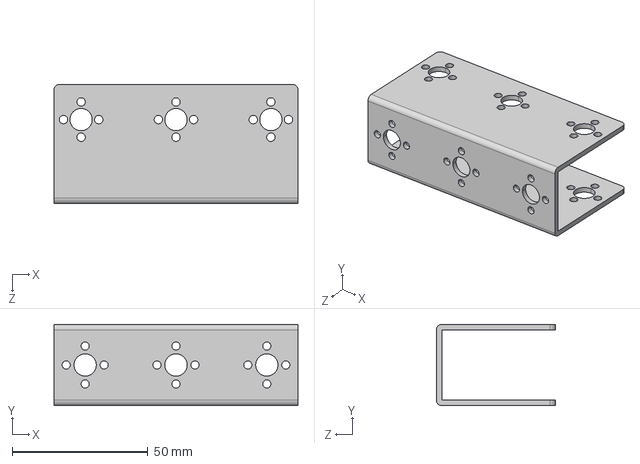
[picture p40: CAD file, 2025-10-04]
Hardware/Datasheets/Servo/TPServo_LX224/3. Servo Manual & Diagram/3. Drawings/Bracket/IGS/U beam.IGS
90.0 x 30.0 x 44.0 mm

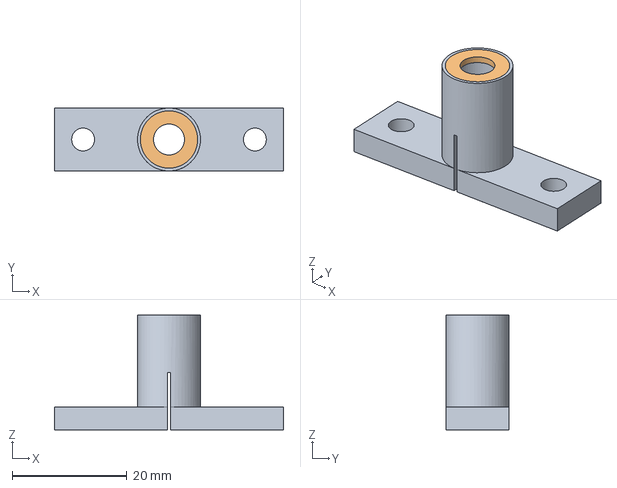
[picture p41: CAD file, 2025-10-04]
Hardware/3D_Print/smoke_bottom.FCStd
40.0 x 11.0 x 20.0 mm
Tube

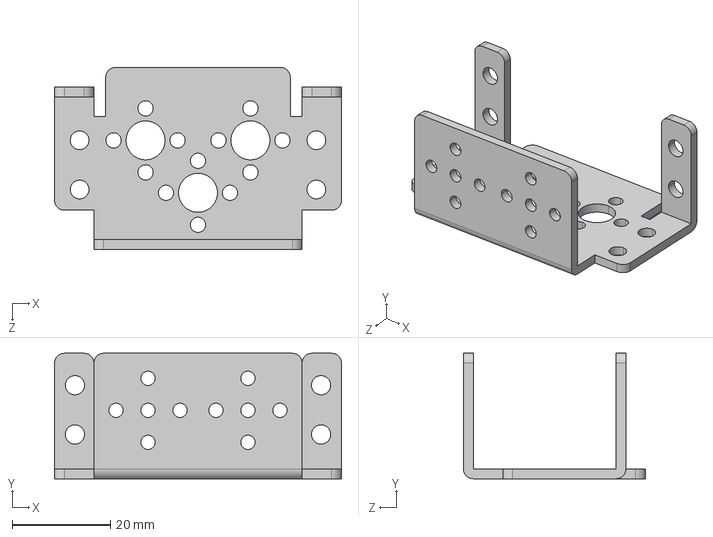
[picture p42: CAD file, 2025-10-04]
Hardware/Datasheets/Servo/TPServo_LX224/3. Servo Manual & Diagram/3. Drawings/Bracket/IGS/Multi-functional bracket.IGS
58.3 x 25.5 x 37.0 mm

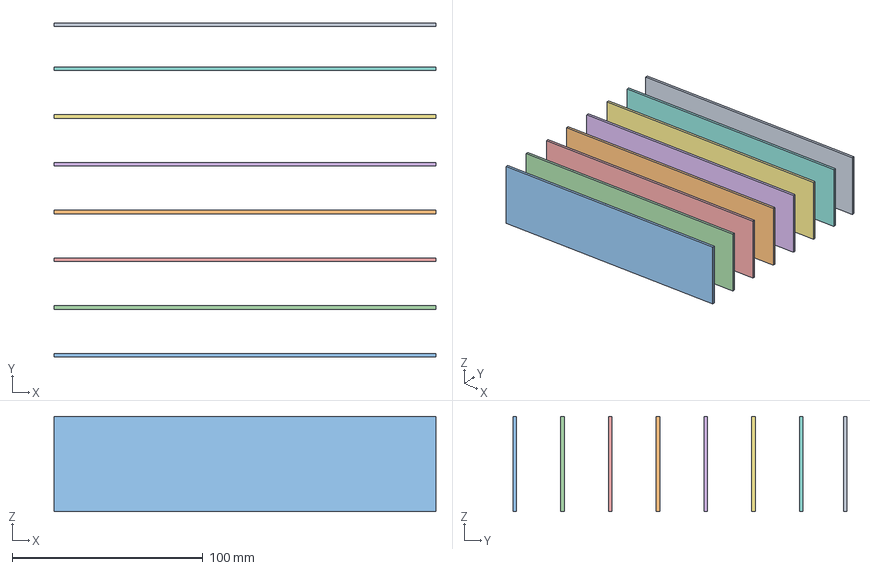
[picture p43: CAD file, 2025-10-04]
Hardware/3D_Print/CMesh.FCStd
200.0 x 175.0 x 50.0 mm

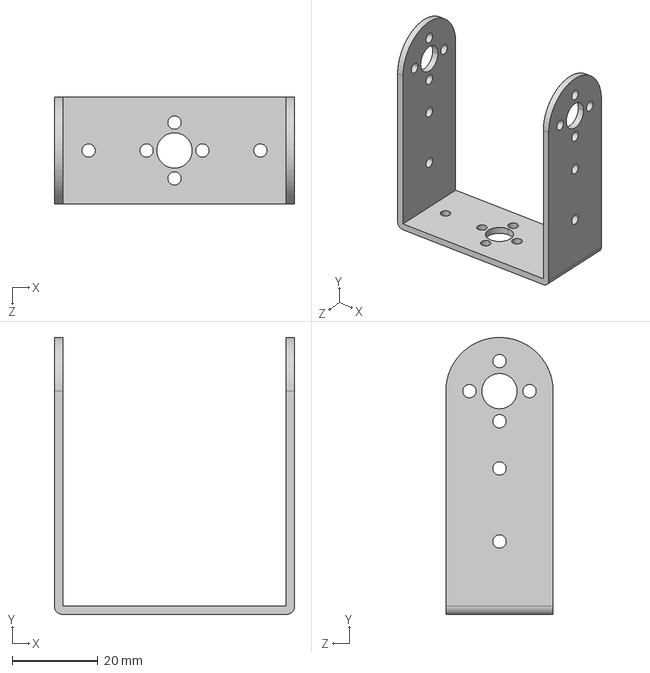
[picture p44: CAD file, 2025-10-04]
Hardware/Datasheets/Servo/TPServo_LX224/3. Servo Manual & Diagram/3. Drawings/Bracket/IGS/U backet-Long.IGS
56.0 x 64.5 x 25.0 mm

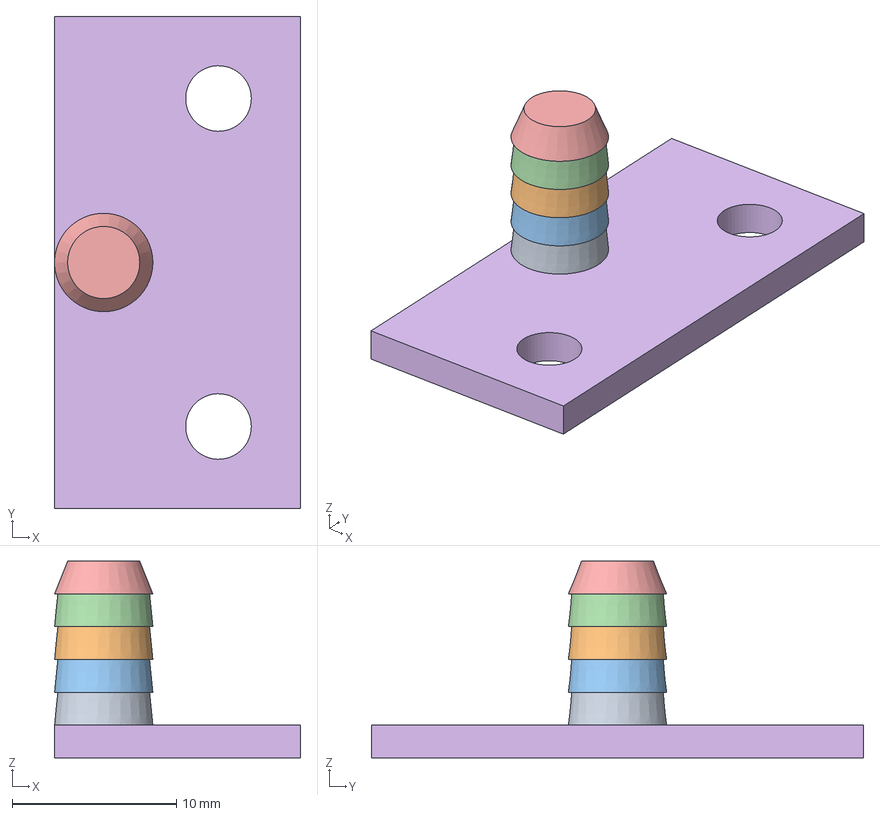
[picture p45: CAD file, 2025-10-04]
Hardware/3D_Print/smoke_top.FCStd
15.0 x 30.0 x 12.0 mm

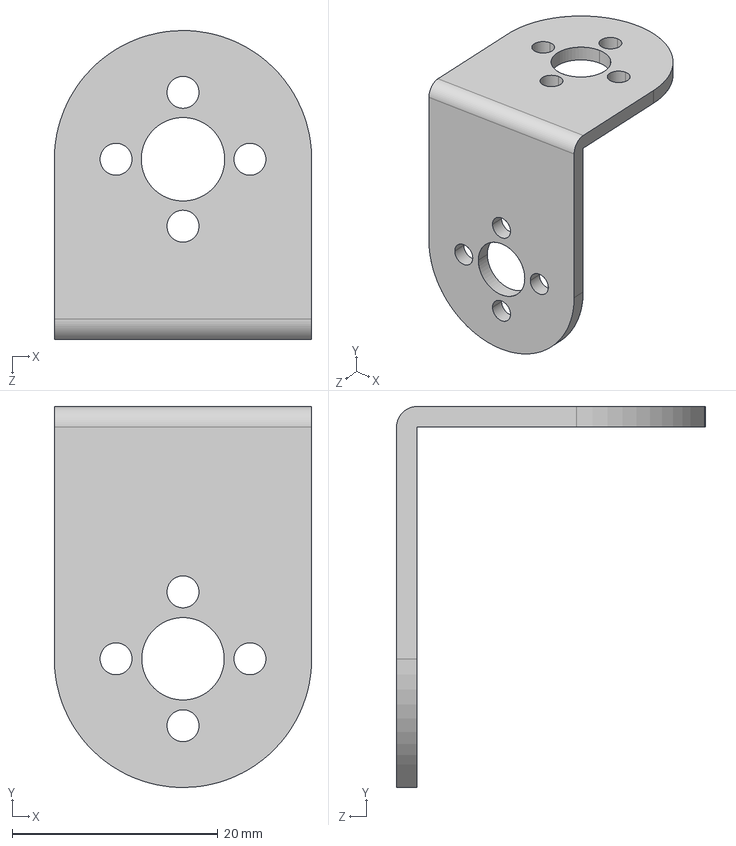
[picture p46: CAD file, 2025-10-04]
Hardware/Datasheets/Servo/TPServo_LX224/3. Servo Manual & Diagram/3. Drawings/Bracket/IGS/L backet.IGS
25.0 x 37.0 x 30.0 mm

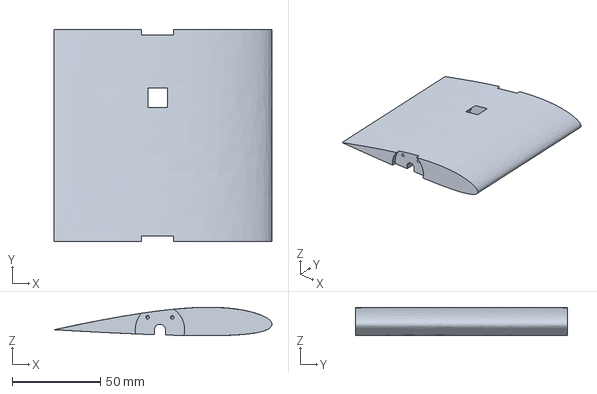
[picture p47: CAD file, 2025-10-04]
Hardware/3D_Print/wing.FCStd
123.5 x 120.0 x 16.1 mm

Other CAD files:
Hardware/Datasheets/Servo/TPServo_LX224/3. Servo Manual & Diagram/3. Drawings/LX-224.dwg
Hardware/Datasheets/Servo/TPServo_LX224/3. Servo Manual & Diagram/3. Drawings/Bracket/IGS/Oblique U bracket.IGS
Hardware/3D_Print/smokePipeClamp.FCStd
Hardware/Datasheets/Servo/TPServo_LX224/3. Servo Manual & Diagram/3. Drawings/Bracket/IGS/Footboard.IGS
Hardware/3D_Print/CMesh.stl
Hardware/3D_Print/light_strip.stl
Hardware/3D_Print/smokePipeClamp.stl
Hardware/3D_Print/smokePipeClamp2.stl
Hardware/3D_Print/smoke_bottom.stl
Hardware/3D_Print/smoke_top.stl
Hardware/3D_Print/smoker.stl
Hardware/3D_Print/wing.stl
Hardware/Datasheets/Servo/TPServo_LX224/3. Servo Manual & Diagram/3. Drawings/Bracket/DXF/Footboard.DXF
Hardware/Datasheets/Servo/TPServo_LX224/3. Servo Manual & Diagram/3. Drawings/Bracket/DXF/L backet.DXF
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

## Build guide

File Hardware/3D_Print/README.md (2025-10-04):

# 3D Print Files

This directory contains 3D printable files for the wind tunnel project.

| Component Name | Purpose | STL File | FCStd File |
|----------------|---------|----------|------------|
| CMesh | Airflow straightener | [CMesh.stl](CMesh.stl) | [CMesh.FCStd](CMesh.FCStd) |
| light_strip | Hold the light strip on the top of test cover | [light_strip.stl](light_strip.stl) | [light_strip.FCStd](light_strip.FCStd) |
| smoke_bottom | Hold smoke pipe bottom | [smoke_bottom.stl](smoke_bottom.stl) | [smoke_bottom.FCStd](smoke_bottom.FCStd) |
| smoke_top | Hold smoke pipe top | [smoke_top.stl](smoke_top.stl) | [smoke_top.FCStd](smoke_top.FCStd) |
| smokePipeClamp | Hold smoke tube on the contraction | [smokePipeClamp.stl](smokePipeClamp.stl) | [smokePipeClamp.FCStd](smokePipeClamp.FCStd) |
| smokePipeClamp2 | Hold smoke tube on the contraction | [smokePipeClamp2.stl](smokePipeClamp2.stl) | [smokePipeClamp2.FCStd](smokePipeClamp2.FCStd) |
| smoker | Hold Smoke Generator | [smoker.stl](smoker.stl) | [smoker.FCStd](smoker.FCStd) |
| Wing | Wing for test | [wing.stl](wing.stl) | [wing.FCStd](wing.FCStd) |

## File Types

- **STL Files**: Ready-to-print 3D STL files
- **FCStd Files**: FreeCAD project files of the original design

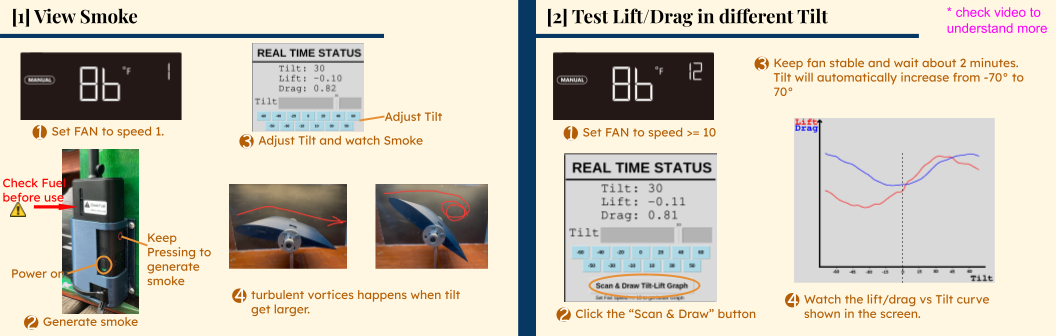
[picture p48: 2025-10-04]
docs/User_Guide.png

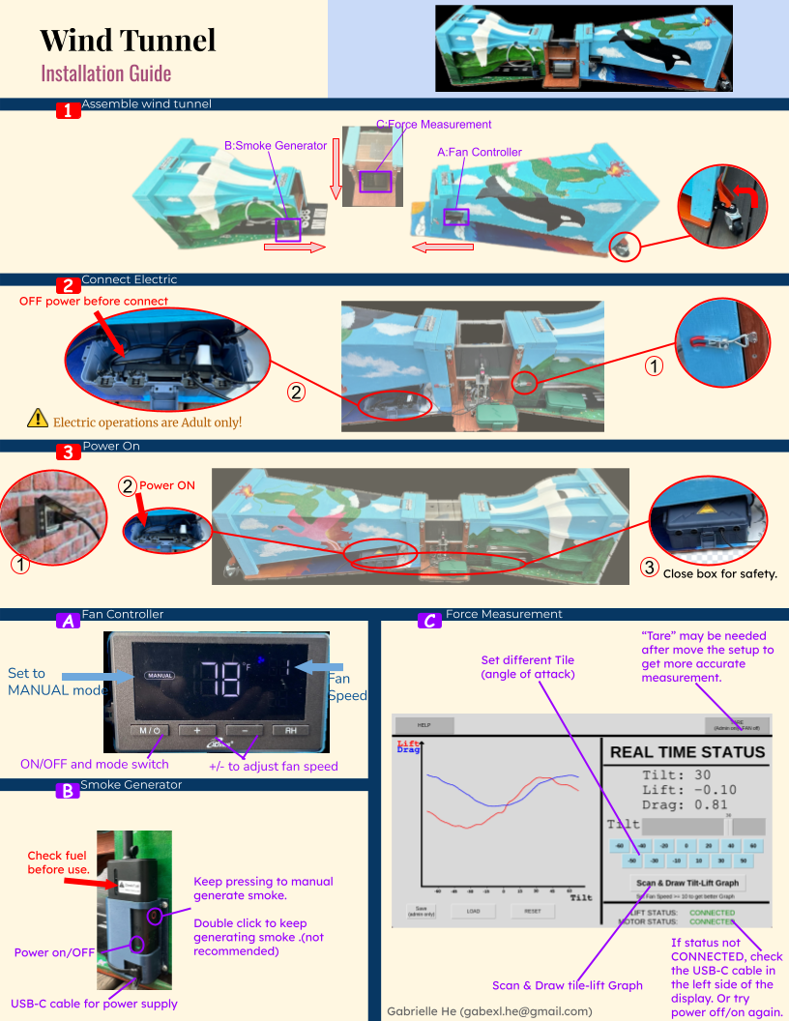
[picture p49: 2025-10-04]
docs/Installation_Guide.png

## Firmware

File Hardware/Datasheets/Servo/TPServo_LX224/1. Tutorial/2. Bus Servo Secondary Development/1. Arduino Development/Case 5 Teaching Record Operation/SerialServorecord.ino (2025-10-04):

#include "include.h"
#include "SerialServo.h"

#define KEY1   2    //定义按键1(define button 1)
#define KEY2   4    //定义按键2(define button 2)

void setup() {
  Serial.begin(115200);
  pinMode(2, INPUT_PULLUP);
  pinMode(4, INPUT_PULLUP);
  delay(1000);
}

int id;

void loop() {
   static bool run = false;
  static char step = 0;
  static char mode = 0;
  static int pos[4] = {100,200,300,400};
  uint16_t temp;
  id = LobotSerialServoReadID(Serial);
  while (1) {
    if (mode == 0)
    {
      if (run)
      {
        LobotSerialServoMove(Serial, id, pos[step++], 500);
        if (step == 4)
        {
          step = 0;
          run = false;
        }
        delay(1000);
      }
      if (!digitalRead(KEY2))
      {
        delay(10);
        if (!digitalRead(KEY2))
        {
          run = true;
          step = 0;
          delay(500);
        }
      }
      if (!digitalRead(KEY1))
      {
        delay(10);
        if (!digitalRead(KEY1))
        {
          LobotSerialServoUnload(Serial, id);
          mode = 1;
          step = 0;
          delay(500);
        }
      }
    }
    if (mode == 1)
    {
      if (!digitalRead(KEY2))
      {
        delay(10);
        if (!digitalRead(KEY2))
        {
          pos[step++] = LobotSerialServoReadPosition(Serial, id);
          if (step == 4)
            step = 0;
          delay(500);
        }
      }
      if (!digitalRead(KEY1))
      {
        delay(10);
        if (!digitalRead(KEY1))
        {
          temp = LobotSerialServoReadPosition(Serial, id);
          LobotSerialServoMove(Serial, id, temp, 200);
          mode = 0;
          delay(500);
        }
      }
    }
  }
}

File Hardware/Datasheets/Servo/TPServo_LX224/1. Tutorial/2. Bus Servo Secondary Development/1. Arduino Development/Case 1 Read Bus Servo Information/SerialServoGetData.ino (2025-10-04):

#include "include.h"
#include "SerialServo.h"

void setup() {
  Serial.begin(115200);
  delay(1000);
}

void loop() {
  int id = LobotSerialServoReadID(Serial);  //读取当前舵机ID(read current servo ID)
  int pos = LobotSerialServoReadPosition(Serial, id); //读取舵机实时位置(read servo real-time position)
  int dev = LobotSerialServoReadDev(Serial, id);  //读取舵机偏差，默认0(Read servo deviation, which is 0 by default)
  LobotSerialServoReadAngleRange(Serial, id);   //读取舵机角度限位，默认（0-1000）(Read servo angle limit, which is 0 to 1000 by default)
  LobotSerialServoReadVinLimit(Serial, id); //读取电压限制范围，默认（4.50-14.00V）(Read voltage limit range, which is 4.50 to 14.00V by default)
  int temperature_warn = LobotSerialServoReadTempLimit(Serial, id); //读取温度报警阈值，默认（85°）(Read temperature alarm threashold, which is 85 degrees by default)
  int temperature = LobotSerialServoReadTemp(Serial, id); //读取舵机实时温度(read servo's real-time temperature)
  int vin = LobotSerialServoReadVin(Serial, id);  //读取舵机实时电压(read servo's real-time voltage)
  int lock = LobotSerialServoReadLoadOrUnload(Serial, id);  //读取舵机状态(read servo status)
  Serial.println("");
  Serial.print("id:");
  Serial.println(id);
  Serial.print("pos:");
  Serial.println(pos);
  Serial.print("dev:");
  Serial.println(dev);
  Serial.print("angle_range:");
  Serial.print(retL);
  Serial.print("-");
  Serial.println(retH);
  Serial.print("vin_range:");
  Serial.print((float)vinL/1000);
  Serial.print("-");
  Serial.print((float)vinH/1000);
  Serial.println(" V");
  Serial.print("temperature_warn:");
  Serial.println(temperature_warn);
  Serial.print("temperature:");
  Serial.println(temperature);
  Serial.print("vin:");
  Serial.println((float)vin/1000);
  Serial.print("lock:");
  Serial.println(lock);
  delay(1000);
}

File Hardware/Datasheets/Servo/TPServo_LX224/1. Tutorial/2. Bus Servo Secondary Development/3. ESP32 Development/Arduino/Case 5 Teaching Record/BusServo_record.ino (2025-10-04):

#include "LobotSerialServoControl.h" // 导入库文件(import library file)

// 控制总线舵机转动例程(bus servo rotation control program)

#define SERVO_SERIAL_RX   35
#define SERVO_SERIAL_TX   12
#define receiveEnablePin  13
#define transmitEnablePin 14
HardwareSerial HardwareSerial(2);
LobotSerialServoControl BusServo(HardwareSerial,receiveEnablePin,transmitEnablePin);

void setup() {
  // put your setup code here, to run once:
  Serial.begin(9600); // 设置串口波特率(set baud rate of serial port)
  Serial.println("start...");  // 串口打印"start..."(serial port prints "start...")
  BusServo.OnInit();
  HardwareSerial.begin(115200,SERIAL_8N1,SERVO_SERIAL_RX,SERVO_SERIAL_TX);
  delay(500); // 延时500毫秒(delay for 500ms)
}
bool start_en = true;

void loop() {
  if (start_en) {
    Serial.print("ID: ");
    Serial.println(BusServo.LobotSerialServoReadID(0xFE)); // 获取舵机ID并通过串口打印(obtain servo ID and print via serial port)
    delay(500); // 延时(delay)
    
    uint8_t ID =BusServo.LobotSerialServoReadID(0xFE);
    
    BusServo.LobotSerialServoMove(ID,500,1000); // 设置舵机运行到500脉宽位置，运行时间为1000毫秒(Set the servo to rotate to the position with pulse width 500 in 1000ms)
    delay(1000); // 延时1000毫秒(delay for 1000ms)
    
    Serial.println("Start turning the servo");
    BusServo.LobotSerialServoUnload(ID);//设置舵机掉电三秒钟(set the servo to power off for 3s)
    delay(3000); // 延时3000毫秒(delay for 3000ms)
    
    int16_t position=BusServo.LobotSerialServoReadPosition(ID);// 获取舵机现在的脉宽位置，运行时间为2000毫秒(obtain the current pulse width position of the servo, with the runtime of 2000ms)
    delay(2000); // 延时2000毫秒(delay for 2000ms)
    BusServo.LobotSerialServoMove(ID,500,1000); // 设置舵机运行到500脉宽位置，运行时间为1000毫秒(Set the servo to rotate to the position with pulse width 500 in 1000ms)
    delay(2000); // 延时2000毫秒(delay for 2000ms)

    BusServo.LobotSerialServoMove(ID,position,1000); // 设置舵机运行到上一次的脉宽位置，运行时间为1000毫秒(Set the servo to rotate to the position with previous pulse width in 1000ms)
    delay(1000); // 延时1000毫秒(delay for 1000ms)
    
    start_en = false;
  }
  else {
    delay(500); // 延时500毫秒(delay for 500ms)
  }
} 
